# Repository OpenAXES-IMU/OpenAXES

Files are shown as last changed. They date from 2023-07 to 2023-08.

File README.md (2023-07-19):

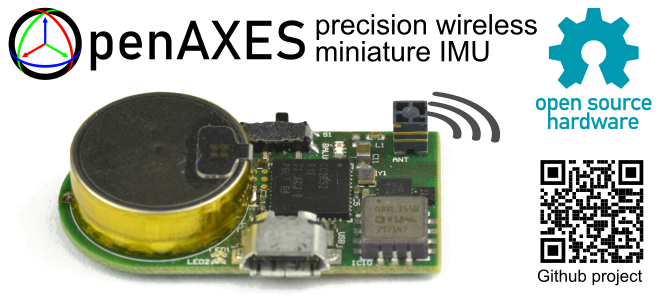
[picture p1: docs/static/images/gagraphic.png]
OpenAXES Graphical Abstract


# OpenAXES

**Hardware design files and source code for an open-access wireless IMU** developed at the [Institute of Microelectronic Systems](https://www.ims.uni-hannover.de/) at the Leibniz University Hannover, Germany.

The OpenAXES IMU is open-source hardware licensed under the CERN-OHL-S-v2+. This means that you are allowed to modify, share, or sell the design, **if** you adhere to the respecitive licenses (see section [License](#license) or [LICENSE.txt](/LICENSE.txt) for details).

If you use the OpenAXES project (or parts of it) in scientific work, please see the [Citation](#citation) section below.

## Hardware

The hardware subdirectory contains the ECAD design files for the OpenAXES PCB and its fabrication outputs, and MCAD files for the housing, the programming adapter, and a calibration fixture.

More information about the hardware and how to fabricate it can be found in [the README in the hardware folder](/hardware/README.md)

## Firmware

The OpenAXES firmware is written in C and based on the CC2652 SDK from Texas Instruments.
It is based on TI-RTOS and can be compiled with [Code Composer Studio (CCS)](https://www.ti.com/tool/CCSTUDIO).

More information on how to compile and flash the firmware can be found in [the README in the firmware folder](/firmware/README.md)

## Citation

If you use the OpenAXES project (or parts of it) in scientific work,
please cite our upcoming paper (**submitted for peer review - not published yet**).

> Title: "OpenAXES: An Open-Source Wireless Inertial Measurement Unit"
>
> Authors: Fritz Webering, Nils Stanislawski, Joseph Winkler, Sarah Kleinjohann, Holger Blume
>
> Journal: [IEEE Sensors Letters](https://ieee-sensors.org/ieee-sensors-letters/)

The correct precise citation will be updated as soon as possible.

# License

Copyright 2023 Nils Stanislawski (nils.stanislawski@ims.uni-hannover.de) and Fritz Webering (fritz.webering@ims.uni-hannover.de)

This documentation describes Open Hardware and is licensed under the CERN-OHL-S-v2 or any later version.

You may redistribute and modify this documentation under the terms of the CERN OHL-S-v2 (https://ohwr.org/cern_ohl_s_v2.txt) or any later version. This documentation is distributed WITHOUT ANY EXPRESS OR IMPLIED WARRANTY, INCLUDING OF MERCHANTABILITY, SATISFACTORY QUALITY AND FITNESS FOR A PARTICULAR PURPOSE. Please see the CERN OHL v2-S for applicable conditions

Source Location: https://github.com/OpenAXES-IMU/OpenAXES

For detailed license information on individual files, please see the file [LICENSE.txt](/LICENSE.txt) in the root folder of this repository.

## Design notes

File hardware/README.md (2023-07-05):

# Hardware

The **Hardware** subdirectory contains the ECAD design files for the OpenAXES PCB and its fabrication outputs, and MCAD files for the housing and calibration fixture.

This documentation describes Open Hardware and is licensed under the CERN-OHL-S v2 or any later version. See [License](#license) below for more information.

## PCB

This directory comprises the Altium Designer and KiCad EDA files. 
Altium Designer is a globally renowned PCB and electronic design software. 
KiCad, on the other hand, is a free open source software suite for EDA. 
The use of these two platforms ensures our project is accessible to a broad range of users.

The OpenAXES hardware platform was originally developed using Altium Designer.
To allow for the use of open source EDA software tools it has been ported to KiCad.
Known differences in the design files are only found in the silkscreen layers, so that there are no restrictions on the underlying functionality of the PCB.

### Getting Started

To work with the files contained in this directory, you will need to have the appropriate software installed on your local machine.

- For Altium files, download and install [Altium Designer](https://www.altium.com/)
- For KiCad files, download and install [KiCad EDA](https://www.kicad.org/)

Once you have installed the appropriate software, clone the repository and navigate to the respective subdirectories to access the project files.

### Fabrication outpus

Fabrication outputs are provided in the _PCB/Altium/Project Outputs for OpenAXES_ subdirectory.
Output files for both single PCB and a panel optimized for mass production are included.
 
### Deprecated components

- **BMI160**; pin-compatible replacement: BMI270

## Housing

The housing for the OpenAXES IMU can be found in the **hardware/case** subdirectory.
It was designed in FreeCAD 0.20 for 3D-printing with a 0.4 mm diameter FDM nozzle.
If the 3D printer is tunes correctly, the two halves of the case will snap together and provide a tight fit for the PCB.

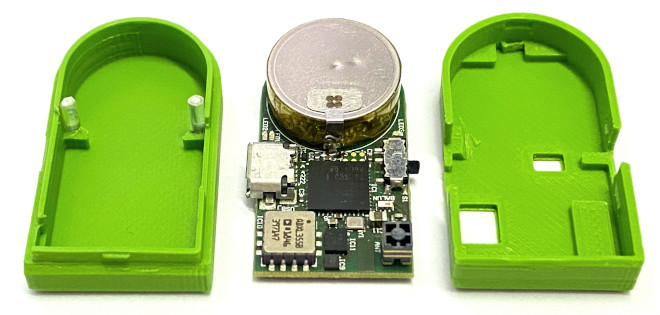
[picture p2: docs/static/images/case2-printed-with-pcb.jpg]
Photograph of the OpenAXES PCB and case


There are cutouts for the USB port, the power switch, the analog pads on the bottom of the PCB, and for the JTAG adapter.
The two holes at the top can be plugged with short pieces of transparent 3D-printing filament (1.75 mm diameter).
These will act as light guides for the top LEDs next to the battery.

## Programming adapter

The programming adapter found in the **hardware/programming-adapter** directory comprises a 3D-printable fixture and a single-layer PCB with spring loaded pins.
These work together with the case, holding the IMU in place and contacting the six pads on the underside of the IMU PCB, for JTAG programming or debugging.

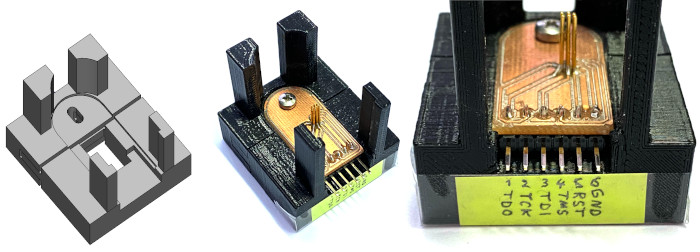
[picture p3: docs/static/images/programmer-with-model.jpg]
3D model and photograph of the programming adapter


The adapter can be used with any JTAG adapter compatible with the CC2652 processor and the Code Composer Studio IDE.
During development, we used the LAUNCHXL-CC26X2R1 evaluation board from TI as a JTAG programmer.
All JTAG signals on that board are accessible on a pin header, which is normally populated with jumpers.
By removing the jumpers, the JTAG interface on the evaluation board can be used for external boards:

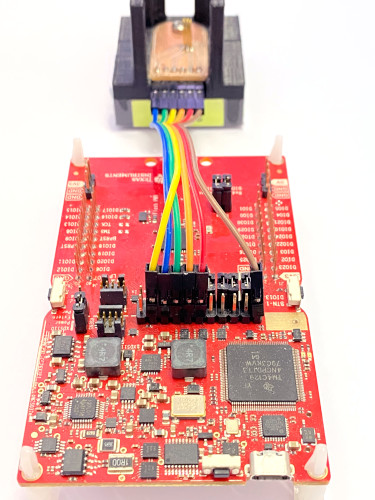
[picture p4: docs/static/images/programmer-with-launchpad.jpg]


## Calibration fixture

The calibration fixture found in **hardware/calibrator** is an icosahedron (20-sided polyhedron) with a recess that accepts the IMU case.
This fixture can be used together the with scripts in the **calibration** directory to obtain the sensor calibration coefficients for each individual unit.

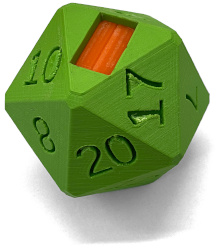
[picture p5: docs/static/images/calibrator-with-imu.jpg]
Photograph of the calibration fixture with an IMU


# License

Copyright 2023 Nils Stanislawski and Fritz Webering

This documentation describes Open Hardware and is licensed under the CERN-OHL-S-v2 or any later version.

You may redistribute and modify this documentation under the terms of the CERN OHL-S-v2 (https://ohwr.org/cern_ohl_s_v2.txt) or any later version. This documentation is distributed WITHOUT ANY EXPRESS OR IMPLIED WARRANTY, INCLUDING OF MERCHANTABILITY, SATISFACTORY QUALITY AND FITNESS FOR A PARTICULAR PURPOSE. Please see the CERN OHL v2-S for applicable conditions

Source Location: https://github.com/IMS-AS-LUH/OpenAXES

For detailed license information on individual files, please see the file [LICENSE.txt](/LICENSE.txt) in the root folder of this repository.

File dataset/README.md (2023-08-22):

# OpenAXES Example Robot Dataset

**Since git repositories are not suitable for storing large amounts of static data, the dataset itself is kept in the research data repository of the LUH: https://doi.org/10.25835/psqqs9w0. This repository just contains the Jupyter Notebook for quick access.**

This dataset was recorded using four OpenAXES IMUs mounted on the segments of a robot arm (UR5 by Universal Robots), as shown in Fig. 4.
The robot arm was programmed to perform a calibration movement, then trace a 2D circle or triangle in the air with its tool center point (TCP), and return to its starting position, at four different speeds from 100 mm/s to 250 mm/s.
This results in a total of 8 different scenarios (2 shapes times 4 speeds).
The ground truth joint angle and TCP position values were obtained from the robot controller.
The calibration movement at the beginning of the measurement allows for calculating the exact orientation of the sensors on the robot arm.

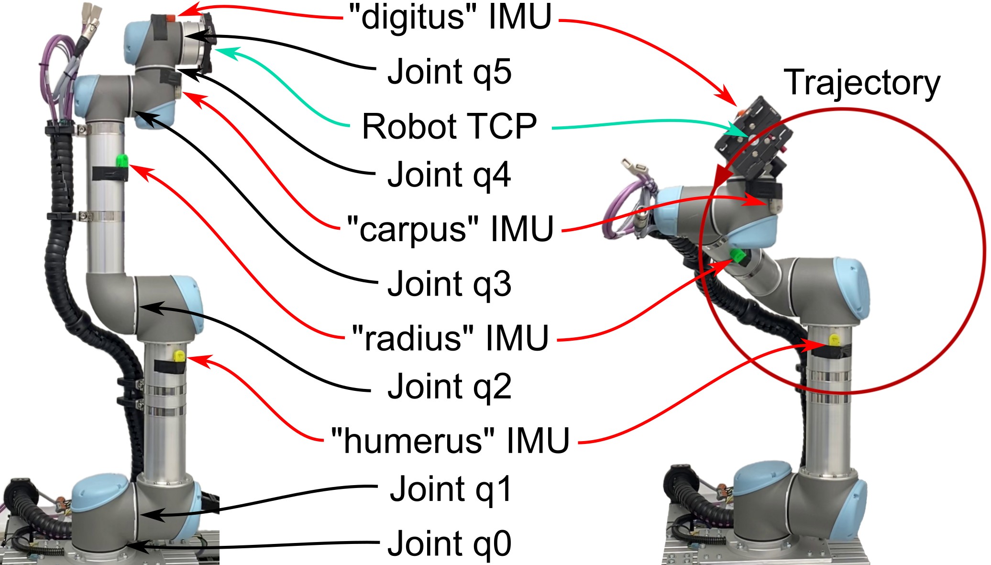
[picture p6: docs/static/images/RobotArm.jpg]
Fig. 4 Setup of the robot arm experiment, showing the four IMUs, the six joints of the robot arm, the tool center position (TCP) and the circle trajectory.
<br>
*Fig. 4  Setup of the robot arm experiment, showing the four IMUs, the six joints of the robot arm, the tool center position (TCP) and the circle trajectory.*

The IMUs were configured to send the raw data from the three gyroscope axes and the six accelerometer axes to a PC via BLE with 16 bit resolution per axis and 100 Hz sample rate.
Since no data packets were lost during this process, this dataset allows comparing and tuning different sensor fusion algorithms on the recorded raw data while using the ground truth robot data as a reference.

In order to visualize the results, the quaternion sequences from the IMUs were applied to the individual segments of a 3D model of the robot arm.
The end of this kinematic chain represents the TCP of the virtual model, which should ideally move along the same trajectory as the ground truth, barring the accuracy of the IMUs.
Since the raw sensor data of these measurements is available, the calibration coefficients can also be applied ex-post.

Since there are are 6 joints but only 4 IMUS, some redundancy must be exploited.
The redundancy comes from the fact that each IMU has 3 rotational degrees of fredom, but each joint has only one:

* The data for `q0` and `q1` are both derived from the orientation of the "humerus" IMU.
* `q2` is the difference<sup>†</sup> between the orientation of the "humerus" and "radius" IMUs.
* `q3` is the difference between the orientation of the "radius" and "carpus" IMUs.
* `q4` is the difference between the orientation of the "carpus" and "digitus" IMUs.
* The joint `q5` does not influence the position of the TCP, only its orientation, so it is ignored in the evaluation.
* <sup>†</sup> *Of course, difference here means not the subtraction of the quaternions but the rotational difference, which is the `R1 * inv(R0)` for two quaternions (or rotations) `R0` and `R1`. The actual code works a bit differently, but this describes the general principle.*

## Data

* Data recorded from the IMUs is in the directory `measure_raw-2022-09-15/`, one folder per scenario.
In those folders, there is one CSV file per IMU.
* Data recorded from the robot arm is in the directory `measure_raw-2022-09-15/robot/`, one CSV and MAT file per scenario.
* Some photos and videos of the recording process can be found in `Media`. Videos are stored in [git lfs](https://git-lfs.com/).

## Evaluation

The file `openaxes-example-robot-dataset.ipynb` is provided to play around with the data in the dataset and demonstrate how the files are read and interpreted.
To use the notebook, set up a Python 3 virtual environment and therein install the necessary packets with `pip install -r resuirements.txt`.
In order to view the graphs contained in the ipynb file, you will most likely have to trust the notebook beforehand, using the following command:

```bash
jupyter trust openaxes-example-robot-dataset.ipynb
```

**Beware:** This notebook is not a comprehensive evaluation and any results and plots shown in the file are not necessarily scientifically sound evidence of anything.

The notebook will store intermediate files in the `measure_raw-2022-09-15` directory, like the quaternion files calculated by the different filters, or the files containing the reconstructed TCP positions.
All intermediate files should be ignored by the file `measure_raw-2022-09-15/.gitignore`.

The generated intermediate files are also provided in the file `measure_raw-2022-09-15.tar.bz2`, in case you want to inspect the generated files without running the the notebook.

## Tools

A number of tools are used in the evaluation notebook.
Below is a short overview, but not a complete specification.
If you need to understand the input and output formats for each tool, please read the code.

* The file `calculate-quaternions.py` is used in the evaluation notebook to compute different attitude estimation filters like Madgwick or VQF on the raw accelerometer and gyroscrope measurements at 100 Hz.
* The directory `madgwick-filter` contains a small C program that applies the original Madgwick filter to a CSV file containing raw measurements and prints the results. It is used by `calculate-quaternions.py`.
* The file `calculate-robot-quaternions.py` calculates a CSV file of quaternions equivalent to the IMU quaternions from a CSV file containing the joint angles of the robot.
* The program `dsense_vis` mentioned in the notebook is used to calculate the 3D model of the robot arm from quaternions and determine the mounting orientations of the IMUs on the robot arm.
  This program will be released at a future date.
  In the meantime, the output files of `dsense_vis` are provided in the file `measure_raw-2022-09-15.tar.bz2`, which contains the complete content of the `measure_raw-2022-09-15` directory after executing the whole notebook.
  Just unpack this archive and merge its contents with the `measure_raw-2022-09-15` directory.
  This allows you to explore the reconstructed TCP files for the filters implemented at the time of publication.

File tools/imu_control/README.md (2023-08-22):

# OpenAXES IMU Tools

This directory contains scripts to communicate with, control, and configure the OpenAXES IMU.

This documentation describes Open Hardware and is licensed under the CERN-OHL-S v2 or any later version. See [License](#license) below for more information.

# Usage of imu_control.py

The `imu_control` script can be used to control the OpenAXES IMU via the Bluetooth Low Energy (BLE) GATT interface.
It also serves as a demonstration how to implement other clients for the GATT interface.

The main features of the script are:
* selecting which measurement data the IMU should send
* receiving measurement data from the IMU via BLE notifications
* recording the measurement data in CSV files
* passing the IMU data on to other processes via UDP
* showing status information like battery state or firmware version
* configuring the IMU, for example the calibration coefficients
* assistive functions for recording calibration datasets

## Prerequisites

* Use a Linux PC (preferably a modern Ubuntu) or VirtualBox and a Bluetooth adapter.
  The ASUS USB-BT400 stick works best in our experience, especially for many simultaneous connections to different IMUs.
  If you use VirtualBox, you can pass through the USB stick to the guest operating system.
* Make sure that gatttool is installed (probably `sudo apt install bluez bluez-tools`)
* Set permissions on hcitool:
  ```
  sudo setcap 'cap_net_raw,cap_net_admin+eip' /usr/bin/hcitool
  ```
  This allows normal users to scan for BLE devices using `hcitool lescan`.
  The udpstream script uses this to set the connection interval using `hcitool lecup ...` to avoid package loss.

## Configuration files

All operations that interact with an IMU expect a BLE MAC address on the command line.
If you do not like to memorize MAC addresses, you can assign arbitrary names to your IMUs and store them in a file called `my_imu_addresses.json` in the following format:
```json
{
    "imu1": "18:04:ED:C4:75:01",
    "imu2": "18:04:ED:C4:75:02"
}
```
These IMU names can then be used on the command line as shown in the examples below.

## Initialize IMUs before each use

* Switch IMUs on.
* Lay IMUs *perfectly still* on a table (LED side up).
* Run `./imu_control.py --reset-sensors imuX` for each IMU. *Do not touch IMUs before all commands completed!*
* IMU initialization is complete. You can now capture data.
  For example, run `./imu_control.py imuX` for each IMU to capture quaternions.
  Make a small pause between starting different IMUs, for example like this:

  ```
  ../imu_control.py imu1
  sleep 0.5
  ../imu_control.py imu2
  sleep 0.5
  ../imu_control.py imu6
  ```

## Lost packets at the start

* At the start of the transmission, some packets may be lost.
  This is normal, because the connection interval is set only a short while after the transmission starts.
* You can skip the first few packets and start recording once the connection is stable:
  `./imu_control.py imuX --skip 100` will skip the first 100 received packets before recording, which is about 1 second.
  Skipped packets will not be reported as "lost".

## Change what type of data is sent

* Reset IMUs (see above).
* Capture data using the `--mode` option.
  For example, `./imu_control.py --mode INDEX,ACCEL_BMI160,GYRO` will record a 16-bit packet index, plus gyroscope and accelerometer data from the BMI160 chip.
* See `./imu_control.py --help` for available data types for `--mode`.

## Battery level

* Battery level is permanently shown by the red blinking LED.
  The duty cycle is equal to the battery level (e.g. 40% on and 60% off means 40% battery level remaining).
* `./imu_control.py imuX -b` or `--battery` will print the battery level before each measurement.
* A WARNING will be printed if the battery level is below 15% when starting a measurement.
* `./imu_control.py imuX --status` will print detailed battery information, like current consumption, voltage, etc.
* The battery is charged via Micro USB. The blue charging LED will turn off when the battery is full.

## Enable/disable calibration

* Calibration coefficients are applied to the raw data by default, if calibration data is found in IMU flash memory.
* Run `./imu_control.py imuX --status` to see `calibration_status`.
  Value `0x00` means disabled, `0x01` means enabled, and anything else is an error.
* Disable use of calibration coefficients (until IMU reboot):
  `./imu_control.py imuX --command USE_CALIBRATION 0` to disable calibration.
* Run `./imu_control.py --command USE_CALIBRATION 1` to enable calibration.
* Write new calibration coefficients to flash memory on the IMU.
  **You must** replace the ones and zeros with the actual calibration coefficients for each unit according to [the calibration instructions](/calibration/README.md).
  ```
  ./imu_control.py imuX --write-calibration-full 'COEFFICIENTS'
  ```
  
  The argument `'COEFFICIENTS'` must be a space-separated and quoted list of 36 floating point numbers.
  These numbers are three 3x3 identity calibration matrices and three 3-element zero bias vectors:
  1. 9 Coefficients in [row-major order](https://en.wikipedia.org/wiki/Row-_and_column-major_order) for the 3x3 ADXL355 accelerometer scale and nonlinearity calibration matrix.
  2. 3 Coefficients for the ADXL355 bias vector.
  3. 9 Coefficients in [row-major order](https://en.wikipedia.org/wiki/Row-_and_column-major_order) for the BMI160 accelerometer scale and nonlinearity calibration matrix.
  4. 3 Coefficients for the BMI160 accelerometer bias vector.
  5. 9 Coefficients in [row-major order](https://en.wikipedia.org/wiki/Row-_and_column-major_order) for the BMI160 gyroscope scale and nonlinearity calibration matrix.
  6. 3 Coefficients for the BMI160 gyroscope bias vector.
* Permanently reset all calibration coefficients to their default uncalibrated state by setting the calibration matrices to identity and the bias vectors to zero with the following command:
  ```
  ./imu_control.py imuX --write-calibration-full '1 0 0  0 1 0  0 0 1   0 0 0   1 0 0  0 1 0  0 0 1   0 0 0   1 0 0  0 1 0  0 0 1   0 0 0'
  ```

# Usage of bleak_imu_control.py

This script is an experimental port of an old version of `imu_control.py` to use Python 3 and [the python package `bleak`](https://bleak.readthedocs.io/en/latest/) instead of `gatttool` invocations.
Since we could not get the `bleak` interface to work reliably with our IMU, we suspended the experiment and continued using the `gatttool` version that worked more or less reliably.

The current version of the script is presented here only for documentation purposes.
It could be used as a starting point in case someone wants to resume the effort of porting to Python 3 with `bleak`.

# License

Copyright 2023 Nils Stanislawski and Fritz Webering

This documentation describes Open Hardware and is licensed under the CERN-OHL-S-v2 or any later version.

You may redistribute and modify this documentation under the terms of the CERN OHL-S-v2 (https://ohwr.org/cern_ohl_s_v2.txt) or any later version. This documentation is distributed WITHOUT ANY EXPRESS OR IMPLIED WARRANTY, INCLUDING OF MERCHANTABILITY, SATISFACTORY QUALITY AND FITNESS FOR A PARTICULAR PURPOSE. Please see the CERN OHL v2-S for applicable conditions

Source Location: https://github.com/IMS-AS-LUH/OpenAXES

For detailed license information on individual files, please see the file [LICENSE.txt](/LICENSE.txt) in the root folder of this repository.

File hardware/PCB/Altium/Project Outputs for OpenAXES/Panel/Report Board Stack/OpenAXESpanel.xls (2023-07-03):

Board Stack Report
Stack Up |  | Layer Stack
Layer | Board Layer Stack | Name | Material | Thickness | Constant
1 |  | Top Paste
2 |  | Top Overlay
3 |  | Top Solder | Solder Resist | 0,010mm | 3,5
4 |  | Top Layer | Copper | 0,035mm
5 |  | Dielectric 1 | PP-016 | 0,115mm | 4,4
6 |  | Dielectric 2 | PP-016 | 0,115mm | 4,4
7 |  | L2 | Copper | 0,035mm
8 |  | Dielectric 3 | Core-032 | 0,356mm | 4,7
9 |  | L3 | Copper | 0,035mm
10 |  | Dielectric 4 | PP-016 | 0,115mm | 4,4
11 |  | Dielectric 5 | PP-016 | 0,115mm | 4,4
12 |  | Bottom Layer | Copper | 0,035mm
13 |  | Bottom Solder | Solder Resist | 0,010mm | 3,5
14 |  | Bottom Overlay
15 |  | Bottom Paste
 | Height : 0,976mm

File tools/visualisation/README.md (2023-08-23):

# IMU Quaternion Visualization

The folder `/tools/visualization/UDP_Quaternion_OpenGL_Visualisation` contains a Qt project to visualize the Quaternions received from an OpenAXES IMU.

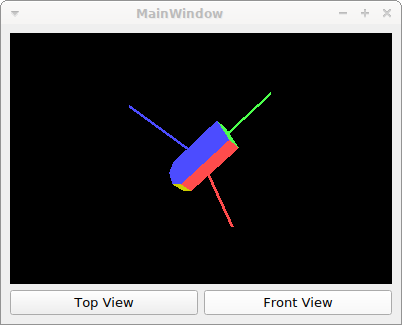
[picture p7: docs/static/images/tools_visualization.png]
Screenshot of visualization software, showing a 3D rendering of the IMU


It receives Quaternions via UDP from the `imu_control.py` script, which will send out one UDP packet to localhost for every received BLE notification.
By default, UDP port 1024 wille, but that can be changed by changing the line `#define UDP_PORT 1024` in `mainwindow.cpp`, and with the second positional command line argument for the script (see `imu_control.py --help`).

From each incoming UDP packet, the four signed 16-bit integers that represent the quaternion will be extracted.
The resulting quaternions will be visualized using a 3D-model of the IMU in OpenGL.

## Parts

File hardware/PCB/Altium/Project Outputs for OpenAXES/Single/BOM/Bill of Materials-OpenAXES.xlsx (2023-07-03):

Line # | Name | Description | Designator | Quantity | Document | Manufacturer 1 | Manufacturer Part Number 1 | Manufacturer Lifecycle 1 | Supplier 1 | Supplier Part Number 1 | Supplier Order Qty 1 | Supplier Unit Price 1 | Supplier Stock 1 | Supplier Packaging 1 | Supplier Subtotal 1 | Case Size/Dimension | Case-EIA | Case-Metric
 | ANTENNA |  | ANT | 1 | C:\Users\Public\Documents\Altium\OpenAXES\SoC.SchDoc | Molex | 47948-0001 |  | Mouser | 538-47948-0001 | 1 | 1.95 | 20907 | Tape & Reel | 1.95
 | 2450BM14G0011 |  | BALUN | 1 | C:\Users\Public\Documents\Altium\OpenAXES\SoC.SchDoc | Johanson | 2450BM14G0011T | Volume Production | Mouser | 609-2450BM14G0011T | 1 | 0.5 | 27734 | Tape & Reel | 0.5
 | CP1654 A3 |  | BAT | 1 | C:\Users\Public\Documents\Altium\OpenAXES\Battery.SchDoc
 | 100n 16V 0402 | CAP 100nF 16V ±10% 0402 (1005 Metric) Thickness 0.6mm SMD | C1, C2, C3, C5, C6, C14, C16, C26, C29, C33, C36, C38, C40, C41, C42, C43, C44 | 17 | C:\Users\Public\Documents\Altium\OpenAXES\SoC.SchDoc, C:\Users\Public\Documents\Altium\OpenAXES\Battery.SchDoc, C:\Users\Public\Documents\Altium\OpenAXES\USB2UART.SchDoc, C:\Users\Public\Documents\Altium\OpenAXES\Sensors.SchDoc | Kyocera AVX | 0402YD104KAT2A | Volume Production | Mouser | 581-0402YD104K | 17 | 0.013 | 3009473 | Tape & Reel | 0.221 |  | 0402 | 1005
 | 10u 6V3 0402 | CAP 10uF 6.3V ±20% 0402 (1005 Metric) Thickness 0.6mm SMD | C4, C21, C22 | 3 | C:\Users\Public\Documents\Altium\OpenAXES\SoC.SchDoc, C:\Users\Public\Documents\Altium\OpenAXES\Battery.SchDoc | Samsung | CL05A106MQ5NUNC | Volume Production | Mouser | 187-CL05A106MQ5NUNC | 3 | 0.24 | 655718 | Tape & Reel | 0.72 |  | 0402 | 1005
 | 12p 10V 0402 | CAP 12pF 10V ±1% 0402 (1005 Metric) Thickness 0.6mm SMD | C7, C8 | 2 | C:\Users\Public\Documents\Altium\OpenAXES\SoC.SchDoc | Vishay Vitramon | VJ0402A120FXQCW1BC |  | Mouser | 77-VJ0402A120FXQCBC | 2 | 0.25 | 8101 | Tape & Reel | 0.5 |  | 0402 | 1005
 | 1p3 10V 0402 | CAP 1.3pF 10V ±0.25pF 0402 (1005 Metric) Thickness 0.6mm SMD | C9 | 1 | C:\Users\Public\Documents\Altium\OpenAXES\SoC.SchDoc | KEMET | CBR04C139B5GAC | Volume Production | Mouser | 80-CBR04C139B5GAC | 1 | 0.16 | 18397 |  | 0.16 |  | 0402 | 1005
 | 1u 16V 0402 | CAP 1uF 16V ±10% 0402 (1005 Metric) Thickness 0.6mm SMD | C10, C20, C23, C30, C31, C34, C35, C37, C39 | 9 | C:\Users\Public\Documents\Altium\OpenAXES\SoC.SchDoc, C:\Users\Public\Documents\Altium\OpenAXES\Battery.SchDoc, C:\Users\Public\Documents\Altium\OpenAXES\Sensors.SchDoc | Taiyo Yuden | EMK105BJ105MVHF | Not Recommended for New Design | Mouser | 963-EMK105BJ105MVHF | 10 | 0.071 | 207971 | Tape & Reel | 0.71 |  | 0402 | 1005
 | CAP 22u 6.3V 0805 | CAP 22uF 6.3V ±10% 0805 (2012 Metric) Thickness 1.45mm SMD | C11 | 1 | C:\Users\Public\Documents\Altium\OpenAXES\SoC.SchDoc | KEMET | C0805C226K9PACTU | Volume Production | Mouser | 80-C0805C226K9PACTU | 1 | 0.35 | 67178 | Tape & Reel | 0.35 |  | 0805 | 2012
 | 4u7 10V 0603 | CAP 4.7uF 10V ±20% 0603 (1608 Metric) Thickness 1mm SMD | C12, C13, C18, C25, C32 | 5 | C:\Users\Public\Documents\Altium\OpenAXES\Battery.SchDoc, C:\Users\Public\Documents\Altium\OpenAXES\USB2UART.SchDoc, C:\Users\Public\Documents\Altium\OpenAXES\Sensors.SchDoc | KEMET | C0603C475M8PACTU | Volume Production | Mouser | 80-C0603C475M8P | 5 | 0.23 | 41855 | Tape & Reel | 1.15 |  | 0603 | 1608
 | 470n 6V3 0402 | CAP 470nF 6.3V ±10% 0402 (1005 Metric) Thickness 0.6mm SMD | C15 | 1 | C:\Users\Public\Documents\Altium\OpenAXES\Battery.SchDoc | Yageo | CC0402KRX5R5BB474 | Volume Production | Mouser | 603-CC402KRX5R5BB474 | 1 | 0.1 | 243770 | Tape & Reel | 0.1 |  | 0402 | 1005
 | 220p 10V 0402 | CAP 220pF 10V ±5% 0402 (1005 Metric) Thickness 0.6mm SMD | C17 | 1 | C:\Users\Public\Documents\Altium\OpenAXES\Battery.SchDoc | Vishay Vitramon | VJ0402Y221JXQCW1BC |  | Mouser | 77-VJ0402Y221JXQCBC | 1 | 0.13 | 17875 | Tape & Reel | 0.13 |  | 0402 | 1005
 | 2u2u 6V3 0402 | CAP 2.2uF 6.3V ±10% 0402 (1005 Metric) Thickness 0.6mm SMD | C19 | 1 | C:\Users\Public\Documents\Altium\OpenAXES\Battery.SchDoc | Kyocera AVX | 04026D225KAT2A | Volume Production | Mouser | 581-04026D225KAT2A | 1 | 0.18 | 126807 | Tape & Reel | 0.18 |  | 0402 | 1005
 | 10n 16V 0402 | CAP 10nF 16V ±10% 0402 (1005 Metric) Thickness 0.33mm SMD | C24 | 1 | C:\Users\Public\Documents\Altium\OpenAXES\USB2UART.SchDoc | Murata | GRM15XR71C103KA86D | Not Recommended for New Design | Mouser | 81-GRM15XR71C103KA6D | 1 | 0.13 | 73728 | Tape & Reel | 0.13 |  | 0402 | 1005
 | 47p 16V 0402 | CAP 47pF 16V ±10% 0402 (1005 Metric) Thickness 0.6mm SMD | C27, C28 | 2 | C:\Users\Public\Documents\Altium\OpenAXES\USB2UART.SchDoc | Vishay Vitramon | VJ0402A470KXJCW1BC |  | Mouser | 77-VJ0402A470KXJCBC | 2 | 0.11 | 18228 | Tape & Reel | 0.22 |  | 0402 | 1005
 | TPD1E10B06DPYR | ESD in 0402 Package with 10 pF Capacitance and 6 V Breakdown, 1 Channel, -40 to +125 degC, 2-pin X2SON (DPY), Green (RoHS & no Sb/Br) | D1, D2 | 2 | C:\Users\Public\Documents\Altium\OpenAXES\USB2UART.SchDoc | Texas Instruments | TPD1E10B06DPYR | Volume Production | Mouser | 595-TPD1E10B06DPYR | 2 | 0.39 | 566012 | Tape & Reel | 0.78
 | CC2652R1FRGZT | CC2650 SimpleLink(TM) Multistandard Wireless MCU, 1.8 to 3.8 V, -40 to 85 degC, 48-Pin VFQFN, Green (RoHS & no Sb/Br), Tape and Reel | IC1 | 1 | C:\Users\Public\Documents\Altium\OpenAXES\SoC.SchDoc | Texas Instruments | CC2652R1FRGZR | Volume Production
 | MCP73830/L |  | IC2 | 1 | C:\Users\Public\Documents\Altium\OpenAXES\Battery.SchDoc | Microchip | MCP73830T-2AAI/MYY | Volume Production | Mouser | 579-MCP73830T2AAIMYY | 1 | 1.19 | 49256 | Tape & Reel | 1.19
 | MAX17055ETB+ |  | IC3 | 1 | C:\Users\Public\Documents\Altium\OpenAXES\Battery.SchDoc | Maxim | MAX17055ETB+T | Volume Production | Mouser | 700-MAX17055ETB+T | 1 | 2.65 | 71324 | Tape & Reel | 2.65
 | BQ2970x |  | IC4 | 1 | C:\Users\Public\Documents\Altium\OpenAXES\Battery.SchDoc | Texas Instruments | BQ29700DSET | Volume Production | Mouser | 595-BQ29700DSET | 1 | 1.22 | 2900 | Tape & Reel | 1.22
 | LTC3221EDC | Micropower, Regulated Charge Pump, 1.8 to 5.5 V Vin, Adjustable Vout, 6-pin SON (DC6-6), -40 to 85 degC | IC5 | 1 | C:\Users\Public\Documents\Altium\OpenAXES\Battery.SchDoc | Analog Devices / Linear Technology | LTC3221EDC-5#TRMPBF | Volume Production | Mouser | 584-C3221EDC-5TRMPBF | 1 | 5.48 | 1335 | Tape & Reel | 5.48
 | TPS7A3501 |  | IC6 | 1 | C:\Users\Public\Documents\Altium\OpenAXES\Battery.SchDoc | Texas Instruments | TPS7A3501DRVT | Volume Production | Mouser | 595-TPS7A3501DRVT | 1 | 1.29 | 474 | Tape & Reel | 1.29
 | ECMF02-2AMX6 | Integrated Circuit | IC7 | 1 | C:\Users\Public\Documents\Altium\OpenAXES\USB2UART.SchDoc | STMicroelectronics | ECMF02-2AMX6 | Volume Production | Digi-Key | 497-10773-1-ND | 1 | 0.64 | 82842 | Cut Tape | 0.64
 | FT230XQ-R | USB to Basic UART Interface Chip, UHCI/OHCI/EHCI Compatible, USB 2.0 Compatible, -40 to +85 degC, 16-Pin QFN, Pb-Free, Tape and Reel | IC8 | 1 | C:\Users\Public\Documents\Altium\OpenAXES\USB2UART.SchDoc | FTDI | FT230XQ-R | Volume Production | Mouser | 895-FT230XQ-R | 1 | 2.46 | 83526 | Tape & Reel | 2.46
 | MMC3416XPJ |  | IC9 | 1 | C:\Users\Public\Documents\Altium\OpenAXES\Sensors.SchDoc | Memsic | MMC34160PJ |  | Mouser | 438-MMC34160PJ | 1 | 4.08 | 4100 | Tape & Reel | 4.08
 | ADXL355BEZ | Low Noise, Low Drift, Low Power, 3-Axis MEMS Accelerometer, 2.25 to 3.6 V, -40 to 125 degC, 14-Pin LCC (E-14-1), RoHS, Tray | IC10 | 1 | C:\Users\Public\Documents\Altium\OpenAXES\Sensors.SchDoc | Analog Devices | ADXL355BEZ | Volume Production | Mouser | 584-ADXL355BEZ | 1 | 64.97 | 7122 | Tray | 64.97
 | BMI160 | Small, low Power Inertial Measurement Unit, 1.2 to 3.6 V, -40 to 85 degC, 14-Pin LGA, Halogen-Free, Tape and Reel | IC11 | 1 | C:\Users\Public\Documents\Altium\OpenAXES\Sensors.SchDoc | Bosch | BMI160
 | BMP388 |  | IC12 | 1 | C:\Users\Public\Documents\Altium\OpenAXES\Sensors.SchDoc | Bosch Sensortec | BMP388
 | LQP15MN1N8B02D | Chip Inductor, 1.8 nH, +/- 0.1 nH, 280 mA, -40 to 85 degC, 0402 (1005 Metric), RoHS, Tape and Reel | L1 | 1 | C:\Users\Public\Documents\Altium\OpenAXES\SoC.SchDoc | Murata | LQP15MN1N8B02D | Obsolete | Mouser | 81-LQP15MN1N8B02D | 1 | 0.18 | 38535 | Tape & Reel | 0.18 | 0402
 | 742792605 | SMD EMI Suppression Ferrite Bead WE-CBF, Z = 33 Ohm | L2 | 1 | C:\Users\Public\Documents\Altium\OpenAXES\USB2UART.SchDoc | Wurth Electronics | 742792605 | Volume Production | Mouser | 710-742792605 | 1 | 0.15 | 6553 | Tape & Reel | 0.15
 | GREEN | Generic 0402 LED | LED1 | 1 | C:\Users\Public\Documents\Altium\OpenAXES\SoC.SchDoc | Rohm | SML-P11MTT86R | Volume Production | Mouser | 755-SML-P11MTT86R | 1 | 0.43 | 175055 | Tape & Reel | 0.43
 | RED | Generic 0402 LED | LED2 | 1 | C:\Users\Public\Documents\Altium\OpenAXES\SoC.SchDoc | Rohm | SML-P11VTT86 | Obsolete | Digi-Key | 846-SML-P11VTT86CT-ND | 1 | 0.55 | 20148 |  | 0.55
 | BLUE | Generic 0402 LED | LED3 | 1 | C:\Users\Public\Documents\Altium\OpenAXES\Battery.SchDoc | Rohm | SMLP13BC8TT86 | Obsolete
 | ORANGE | Generic 0402 LED | LED4 | 1 | C:\Users\Public\Documents\Altium\OpenAXES\USB2UART.SchDoc | Rohm | SML-P11DTT86 | Obsolete | Digi-Key | 846-SML-P11DTT86CT-ND | 1 | 0.54 | 42202 |  | 0.54
 | YELLOW | Generic 0402 LED | LED5 | 1 | C:\Users\Public\Documents\Altium\OpenAXES\USB2UART.SchDoc | Rohm | SML-P11YTT86 | Obsolete | Mouser | 755-SML-P11YTT86 | 1 | 0.58 | 19756 | Tape & Reel | 0.58
 | PressureSensor |  | PS | 1 | C:\Users\Public\Documents\Altium\OpenAXES\Sensors.SchDoc
 | 10K 1% 0402 | 10K 0.063W 1% 0402 (1005 Metric) SMD | R1, R2, R3, R9, R23, R24 | 6 | C:\Users\Public\Documents\Altium\OpenAXES\SoC.SchDoc, C:\Users\Public\Documents\Altium\OpenAXES\Battery.SchDoc, C:\Users\Public\Documents\Altium\OpenAXES\Sensors.SchDoc |  |  |  |  |  |  |  |  |  |  |  | 0402 | 1005
 | Jumper 0402 | Jumper 0402 (1005 Metric) | R4, R20, R22 | 3 | C:\Users\Public\Documents\Altium\OpenAXES\SoC.SchDoc, C:\Users\Public\Documents\Altium\OpenAXES\USB2UART.SchDoc | Bourns | CR0402-J/-000GLF | Volume Production | Mouser | 652-CR0402-J/-000GLF | 10 | 0.004 | 4210905 | Tape & Reel | 0.04 |  | 0402 | 1005
 | 3K3 5% 0402 | 3K3 0.063W 5% 0402 (1005 Metric) SMD | R5, R6, R8, R17, R18 | 5 | C:\Users\Public\Documents\Altium\OpenAXES\SoC.SchDoc, C:\Users\Public\Documents\Altium\OpenAXES\Battery.SchDoc, C:\Users\Public\Documents\Altium\OpenAXES\USB2UART.SchDoc | Panasonic | ERJ-2GEJ332X | Volume Production | Mouser | 667-ERJ-2GEJ332X | 10 | 0.015 | 513572 | Tape & Reel | 0.15 |  | 0402 | 1005
 | 1K2 1% 0402 | 1K2 0.063W 1% 0402 (1005 Metric) SMD | R7 | 1 | C:\Users\Public\Documents\Altium\OpenAXES\Battery.SchDoc | Bourns | CR0402-FX-1201GLF | Volume Production | Mouser | 652-CR0402FX-1201GLF | 1 | 0.1 | 773686 | Tape & Reel | 0.1 |  | 0402 | 1005
 | 0R01 5% 0402 |  | R10 | 1 | C:\Users\Public\Documents\Altium\OpenAXES\Battery.SchDoc | Panasonic | ERJ-MFBAF10MX
 | 2K2 5% 0402 | 2K2 0.063W 5% 0402 (1005 Metric) SMD | R11 | 1 | C:\Users\Public\Documents\Altium\OpenAXES\Battery.SchDoc | Panasonic | ERJ-2GEJ222X | Volume Production | Mouser | 667-ERJ-2GEJ222X | 1 | 0.1 | 451901 | Tape & Reel | 0.1 |  | 0402 | 1005
 | 330R 5% 0402 | 330R 0.063W 5% 0402 (1005 Metric) SMD | R12 | 1 | C:\Users\Public\Documents\Altium\OpenAXES\Battery.SchDoc | Yageo | RC0402JR-07330RL | Volume Production | Mouser | 603-RC0402JR-07330RL | 1 | 0.1 | 1083538 | Tape & Reel | 0.1 |  | 0402 | 1005
 | 4M99 1% 0402 | 4M99 0.063W 1% 0402 (1005 Metric) SMD | R13, R14 | 2 | C:\Users\Public\Documents\Altium\OpenAXES\Battery.SchDoc | Yageo | RC0402FR-074M99L | Volume Production | Mouser | 603-RC0402FR-074M99L | 10 | 0.015 | 10310 | Tape & Reel | 0.15 |  | 0402 | 1005
 | 47K 1% 0402 | 47K 0.063W 1% 0402 (1005 Metric) SMD | R15 | 1 | C:\Users\Public\Documents\Altium\OpenAXES\Battery.SchDoc | Yageo | RC0402FR-0747KL | Volume Production | Mouser | 603-RC0402FR-0747KL | 1 | 0.1 | 2650692 | Tape & Reel | 0.1 |  | 0402 | 1005
 | 24K3 1% 0402 | 24K3 0.063W 1% 0402 (1005 Metric) SMD | R16 | 1 | C:\Users\Public\Documents\Altium\OpenAXES\Battery.SchDoc | Bourns | CR0402-FX-2432GLF | Volume Production | Mouser | 652-CR0402FX-2432GLF | 1 | 0.1 | 347312 | Tape & Reel | 0.1 |  | 0402 | 1005
 | 27R 5% 0402 | 27R 0.063W 5% 0402 (1005 Metric) SMD | R19, R21 | 2 | C:\Users\Public\Documents\Altium\OpenAXES\USB2UART.SchDoc | Panasonic | ERJ-2GEJ270X | Volume Production | Mouser | 667-ERJ-2GEJ270X | 10 | 0.015 | 199037 | Tape & Reel | 0.15 |  | 0402 | 1005
 | SWITCH_SPDT |  | S1 | 1 | C:\Users\Public\Documents\Altium\OpenAXES\Battery.SchDoc | Alps Electric | SSSS810701 |  | Mouser | 688-SSSS810701 | 1 | 1.21 | 7180 | Tape & Reel | 1.21
 | DUAL_NMOS |  | T1 | 1 | C:\Users\Public\Documents\Altium\OpenAXES\Battery.SchDoc | ON Semiconductor / Fairchild | FDMA2002NZ | Volume Production | Mouser | 512-FDMA2002NZ | 1 | 0.9 | 1403 | Tape & Reel | 0.9
 | HIRO-ZX62R-B-5P-5 |  | USB | 1 | C:\Users\Public\Documents\Altium\OpenAXES\USB2UART.SchDoc | Hirose | ZX62R-B-5P(30) | Volume Production | Mouser | 798-ZX62R-B-5P30 | 1 | 1.02 | 22445 | Tape & Reel | 1.02
 | CON_6P2R |  | X1 | 1 | C:\Users\Public\Documents\Altium\OpenAXES\SoC.SchDoc
 | NX2016SA-48M |  | Y1 | 1 | C:\Users\Public\Documents\Altium\OpenAXES\SoC.SchDoc | NDK | NX2016SA-48M-EXS00A-CS08718 |  | Mouser | 344-NX2016SA48S08718 | 1 | 0.74 | 3419 | Tape & Reel | 0.74
 | FC-135-32.76 | Crystal Unit, 32 to 77.5 KHz, 0.5 uW, -40 to 85 degC, 2-Pin SMD, RoHS | Y2 | 1 | C:\Users\Public\Documents\Altium\OpenAXES\SoC.SchDoc | Epson | FC-13532.7680KA-AG0 | Volume Production | Mouser | 732-FC135-32.76KAAG0 | 1 | 0.61 | 477751 | Tape & Reel | 0.61

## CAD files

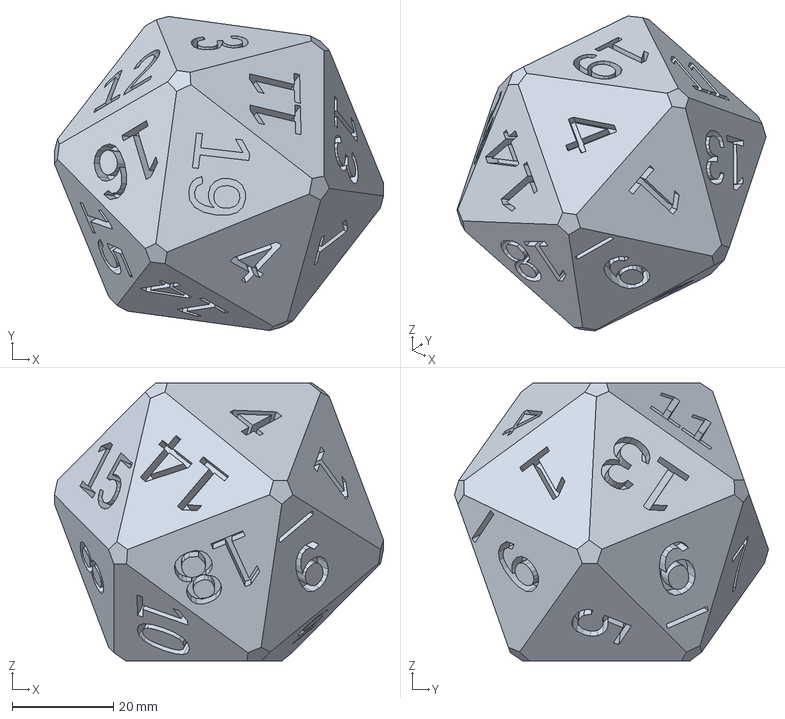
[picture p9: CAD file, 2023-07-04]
hardware/calibrator/D20-Calibrator.3mf
65.2 x 62.1 x 55.0 mm

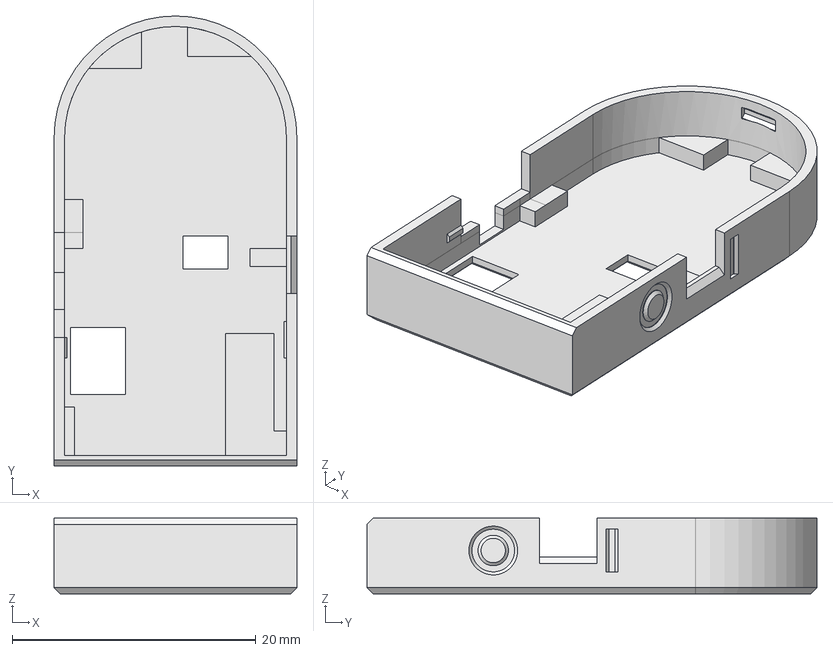
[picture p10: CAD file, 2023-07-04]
hardware/case/IMU-Case2_v12-Bottom.step
19.9 x 36.9 x 6.20 mm

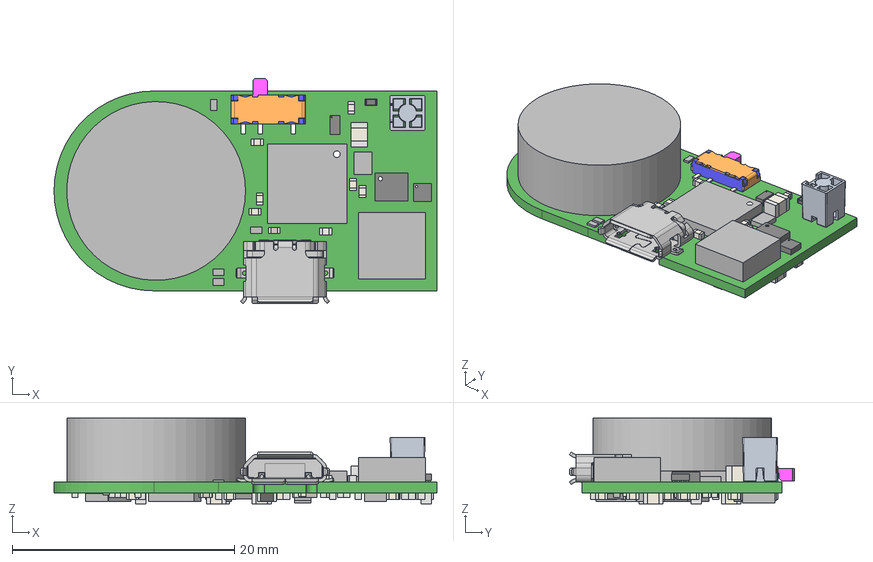
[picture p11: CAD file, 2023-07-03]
hardware/PCB/Altium/Project Outputs for OpenAXES/Single/ExportSTEP/OpenAXES.step
34.5 x 20.3 x 7.74 mm
Extruded x 223
PinsArrayLR
SSSS810701
Pin_Shape x 14
ball x 16
Thermal_Shape x 4
ZX62R-B-5P

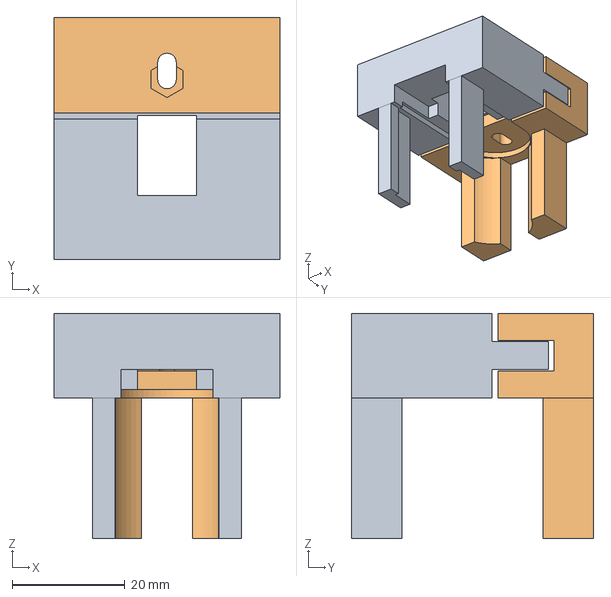
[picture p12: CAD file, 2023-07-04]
hardware/programming-adapter/3D/OpenAXES-Programming-Adapter.step
40.1 x 43.0 x 40.0 mm

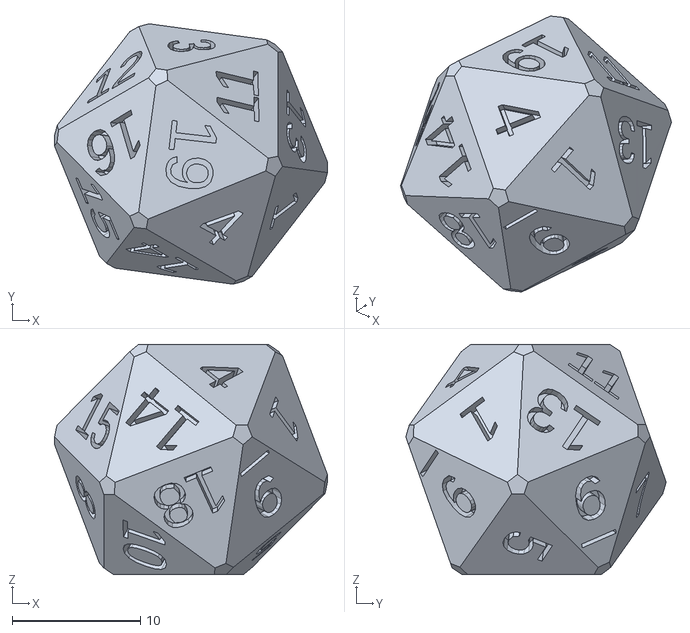
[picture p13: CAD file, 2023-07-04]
hardware/calibrator/sides_20_standard.stl
21.3 x 20.3 x 18.0

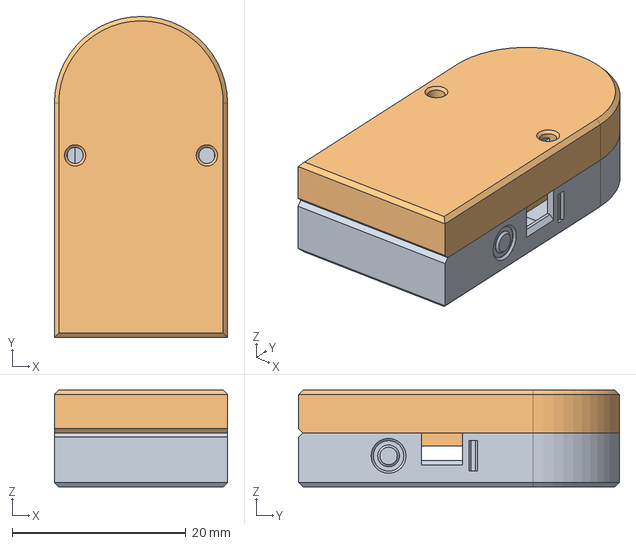
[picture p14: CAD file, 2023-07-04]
hardware/case/IMU-Case2_v12.FCStd
19.9 x 36.9 x 11.1 mm
Bottom
Top

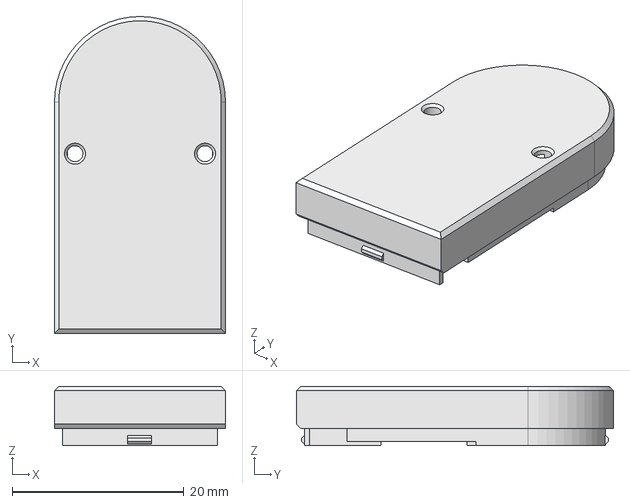
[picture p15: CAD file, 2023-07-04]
hardware/case/IMU-Case2_v12-Top.step
19.9 x 36.9 x 6.90 mm

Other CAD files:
hardware/case/IMU-Case2_v12-Bottom.stl
hardware/case/IMU-Case2_v12-Top.stl
hardware/programming-adapter/3D/OpenAXES-Programming-Adapter.FCStd
hardware/programming-adapter/3D/OpenAXES-Programming-Adapter.stl

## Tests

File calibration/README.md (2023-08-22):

# OpenAXES Calibration Tools and Example Dataset

The `calibration` subdirectory contains the scripts used to calculate the calibration coefficients for OpenAXES IMUs (or any other suitable IMU) using the method published by Tedaldi et al. in their 2014 paper [A robust and easy to implement method for IMU calibration without external equipments][1]

For calibrating our own IMUs we [used the MATLAB implementation by Jianzhu Huai][2] (state as of 2017).
The `imu_tk_matlab` code is included in this repository as a submodule only, because it has no license that would permit us to include a copy of the code itself.
We made some changes, improvements, and bugfixes to the original code, which are contained in the [patches](/calibration/matlab/patches/) subdirectory.
The changes are described in the `CHANGES.md` inside the patch, as well as in greater detail in [our preprint on arxiv.org][3].

Alternatively, one could try to use [the original C++ implementation by Tedaldi et al.][4], which is released under the BSD license.
We used the MATLAB version because it was easier to get started.
We did not test whether it also works with [Octave](https://octave.org/), a free implementation of the MATLAB language.

## Example Calibration Dataset

The subdirectory `/calibration/openaxes_example_calibration_dataset` contains example calibration recordings from four OpenAXES IMUs, which can be used to explore and understand the calibration algorithm.
Please refer to the [separate README file for the dataset](/calibration/openaxes_example_calibration_dataset/README.md) for more information.

**Since git repositories are not suitable for storing large amounts of static data, the dataset itself is kept in the research data repository of the LUH: https://doi.org/10.25835/oimsodoy. Download the dataset from there and extract it into the `/calibration` directory in this repository.**

## Recording Calibration Data

We recommend using the icosahedral calibration fixture for reliable and repeatable recording of calibration data for the OpenAXES IMU.
The 3D-printable model can be found in [the /hardware/calibrator/ directory](/hardware/calibrator/D20-Calibrator.3mf) in 3MF format for PrusaSlicer.

Detailed step-by-step instructions for recording a calibration sequence can be found in [the dataset README file](/calibration/openaxes_example_calibration_dataset/README.md#dataset-recording).

## Calculating Calibration Coefficients

Once calibration recordings have been performed, the `imu_tk` algorithm can be used to calculate the corrective calibration coefficients for that IMU.
We recommend doing a few practice runs before calibrating units for production use.
It is possible and recommended to perform multiple calibration recordings for each IMU and compare the results to make sure they are consistent.
Otherwise, small mistakes in the procedure in one calibration run could result in suboptimal calibration.

To use the MATLAB implementation of the `imu_tk` algorithm, you must first execute the following commands to obtain the patched `imu_tk_matlab` source code:
```bash
# Obtain original imu_tk_matlab code
git submodule update
# Apply changes and fixes to imu_tk_matlab
cd calibration/matlab/imu_tk_matlab
git apply ../patches/*.patch
# Start matlab in calibration directory
cd ../../
matlab
```
This should open MATLAB in the `calibration` directory in this repository (the one containing this README file).

In MATLAB you can run the file `matlab/OpenAXES/do_imu_calibration.m` to calculate the calibration coefficients based on one example recording in `log_imu9_2022-06-22_22-13-55.csv`.
Make sure that you are in the correct folder so that the `imu_tk_matlab` source files can be found somewhere in the matlab search path (see `path(...)` calls).

You can change the `filename` variable in `do_imu_calibration.m` in order to calculate calibration coefficients for your own IMUs.

## Applying Calibration Coefficients to IMUs

After calculating the calibration coefficients, the matlab script should print out command line arguments for `imu_control.py`, which can be used to permanently write the calculated coefficients to your IMU.
The following command line should be printed out for the example recording `log_imu9_2022-06-22_22-13-55.csv`:
```
imu_control.py imu9 --write-calibration-full="0.96276 0 0 0.0015751 0.96732 0 -0.00018891 0.000859 0.97079 0.064447 0.011034 0.034253 0.95418 0 0 0.0031573 0.96061 0 0.009235 0.00049713 0.9501 -0.033224 0.080497 0.01579 0.97288 0.0076747 -0.0063582 -0.011829 1.0062 -0.00033403 0.010087 0.00029571 1.0068 -0.00020494 0.00063007 -0.00036962"
```

Since the coefficients are stored in flash memory, they are retained across resets.
When restarting the IMU, the calibration coefficients should automatically be loaded from flash and applied to all measurements (raw data and quaternions), unless disabled via the corresponding GATT interface via `imu_control.py`.

More information about `imu_control.py` (e.g. enabling, disabling, or checking the current calibration status) can be found in [the corresponding README in `/tools/imu_control/`](/tools/imu_control/README.md).

## Contributing Changes to imu_tk_matlab

As mentioned above, the lack of a license in `imu_tk_matlab` project means that we can not include its source code into this repository, just our changes.
If you change anything in `imu_tk_matlab` and want to contribute your changes to the OpenAXES repository, please use the following procedure:

1. Commit your changes by using git inside the submodule folder `imu_tk_matlab`
2. Inside the submodule folder, run `git format-patch origin/master -o ../patches/`
3. Commit all new `.patch` files that were created into the OpenAXES repository.
4. Do _**NOT**_ <s>`git add imu_tk_matlab`</s>

[1]: https://doi.org/10.1109/ICRA.2014.6907297 "Paper 'A robust and easy to implement method for IMU calibration without external equipments' by Tedaldi et al."
[2]: https://github.com/JzHuai0108/imu_tk_matlab "Matlab scripts of David Tedaldi's ICRA14 paper, a robust and easy to implement method for IMU calibration by Jianzhu Huai"
[3]: https://arxiv.org/pdf/2207.04801.pdf "Preprint 'Improved Calibration Procedure for Wireless Inertial
Measurement Units without Precision Equipment' by Webering et al."
[4]: https://bitbucket.org/alberto_pretto/imu_tk "The original imu_tk C++ implementation"

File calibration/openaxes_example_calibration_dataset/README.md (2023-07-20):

# OpenAXES Example Calibration Dataset

**Since git repositories are not suitable for storing large amounts of static data, the dataset itself is kept in the research data repository of the LUH: https://doi.org/10.25835/oimsodoy. Download the dataset from there and extract it into the `/calibration` directory in this repository.**

This dataset contains calibration sequences of four OpenAXES IMUs, which were performed using the icosahedral calibration fixture described in the OpenAXES repository and paper.
For each IMU, five logs were recorded using the icosahedral calibration fixture according to the procedure described [below](#dataset-recording).
These can be found in the `logs` subdirectory.

Additionally, the `cuboid_logs` directory contains two logs for each IMU in which the device was only placed on the flat faces of the 3D-printed case.
As stated in the preprint, these are not useful for calibration and yield no usable calibration results.
They are only provided for completeness.

The `openaxes_example_calibration_dataset` subdirectory also contains the MATLAB scripts which were used to evaluate the dataset for [our preprint][3].
The script `coefficients-from-mat-files.py` can be used to extract the calibration coefficients from the `.mat` files.

## Evaluation

The `matlab_eval` subdirectory contains the scripts used to calculate the evaluation data presented in [our preprint][3].
To run it, you need the patched `imu_tk_matlab` code from the [OpenAXES repository](https://github.com/OpenAXES-IMU/OpenAXES) see the file [`/calibration/README.md`](https://github.com/OpenAXES-IMU/OpenAXES/blob/main/calibration/README.md) there.

## Dataset Recording

The example dataset was recorded for all four IMUs according to the procedure detailed below.

1. Make the environment as still as possible, for example:
   1. Choose a stury surface on which to perform the calibration, i.e. not a flimsy table that vibrates and sways with each touch.
   2. Avoid touching the surface on which you are working during the whole calibration procedure.
   3. Avoid walking around or moving on your chair during the whole calibration procedure.
   4. Remove all other people and other sources of movement from the room.
2. Insert the IMU into the 3D-printed case
3. Insert the case fully into the calibration fixture
4. Place the fixture on a flat surface in front of the operator who will perform the calibration movements
   A. Place the face with digit 1 facing upwards toward the ceiling
   B. Orient the digit 1 such that the operator can read it naturally (top side of the digit facing away from the operator).
5. Start recording the data with the following command:
   ```
   imu_control.py  imuX -b --still=3 --reset --skip=50 --mode=INDEX,ACCEL_ADXL355,ACCEL_BMI160,GYRO
   ```
   This command will start recording the raw accelerometer and gyroscope data from both inertial sensor chips on the IMU, along with an increasing 16 bit counter.
   * The argument `imuX` must be substituted with the designator of the IMU that is to be calibrated.
   * The flag `-b` will print battery state information to the console before the measurement starts.
   * The flag `--reset` will reset the internal state of the IMU before starting the measurement, specifically: *
     * Re-initialize the sensor ICs, e.g. performing gyroscope offset compensation
     * Reset the quaternion by calculating a new initial quaternion from the accelerometer data.
     * Reset the 16 bit INDEX counter
   * The argument `--still=3` emit a beeping sound when the IMU has lain still for 3 seconds after the last detected movement, prompting the operator to perform the next movement.
   * The argument `--skip=50` will discard the first 50 GATT notifications received, which corresponds to about half a second of data.
     This is necessary because the likelihood of packet loss is far greater at the beginning of the transmission due to unknown reasons.
6. Leave the IMU still on the surface for 40 seconds
7. Rotate the icosahedron such that the next numbered side faces up and is oriented correctly readable for the operator.
   * (_note:_ face number 2 contains the cutout for the IMU case and has no number)
   * It is helpful to draw a small arrow on each face, which points in the general direction of the next number, to speed up the time needed to find the correct face.
   * The movements should be practiced a few times to ensure smooth execution, because long periods of fumbling will increase the total calibration time, which might decrease the accuracy of the method.
8. Place the rotated icosahedron back on the flat surface and let it rest completely motionless until the beeping sound indicates that the static phase has been detected.
9. Again, make sure not to touch the table, walk around, or move on your chair during the still phase.
10. Repeat steps 7-9 for the next numbered face up until number 20.
11. After the first 20 faces, repeat steps 6-7 another 17-20 times, but rotate the icosahedron to a random face instead of the next numbered face.
12. After 37-40 faces, stop the recording by pressing `Ctrl+C` in the terminal running `imu_control.py`.

[1]: https://doi.org/10.1109/ICRA.2014.6907297 "Paper 'A robust and easy to implement method for IMU calibration without external equipments' by Tedaldi et al."
[2]: https://github.com/JzHuai0108/imu_tk_matlab "Matlab scripts of David Tedaldi's ICRA14 paper, a robust and easy to implement method for IMU calibration by Jianzhu Huai"
[3]: https://arxiv.org/pdf/2207.04801.pdf "Preprint 'Improved Calibration Procedure for Wireless Inertial
Measurement Units without Precision Equipment' by Webering et al."
[4]: https://bitbucket.org/alberto_pretto/imu_tk "The original imu_tk C++ implementation"

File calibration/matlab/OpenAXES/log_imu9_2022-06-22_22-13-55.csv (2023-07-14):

MAC | IMU | TIME | INDEX | QUATERNION_0 | QUATERNION_1 | QUATERNION_2 | QUATERNION_3 | ACCEL_ADXL355_0 | ACCEL_ADXL355_1 | ACCEL_ADXL355_2 | ACCEL_BMI160_0 | ACCEL_BMI160_1 | ACCEL_BMI160_2 | GYRO_0 | GYRO_1 | GYRO_2 | GYRO_ECC_0 | GYRO_ECC_1 | GYRO_ECC_2
18:04:ED:C4:75:1A | imu9 | 1655928838621431 | 51 | 0.000000 | 0.000000 | 0.000000 | 0.000000 | -0.063125 | 10.148750 | 0.255000 | -0.245000 | 10.262500 | 0.184375 | 0.000000 | 0.001065 | 0.000000 | 0 | 0 | 0
18:04:ED:C4:75:1A | imu9 | 1655928838636508 | 52 | 0.000000 | 0.000000 | 0.000000 | 0.000000 | -0.048750 | 10.162500 | 0.234375 | -0.252500 | 10.268750 | 0.203125 | 0.000000 | 0.001065 | -0.001065 | 0 | 0 | 0
18:04:ED:C4:75:1A | imu9 | 1655928838644102 | 53 | 0.000000 | 0.000000 | 0.000000 | 0.000000 | -0.030000 | 10.154375 | 0.239375 | -0.264375 | 10.288125 | 0.220625 | -0.001065 | 0.000000 | -0.001065 | 0 | 0 | 0
18:04:ED:C4:75:1A | imu9 | 1655928838651603 | 54 | 0.000000 | 0.000000 | 0.000000 | 0.000000 | -0.048125 | 10.166250 | 0.279375 | -0.236875 | 10.261250 | 0.239375 | 0.000000 | 0.000000 | -0.001065 | 0 | 0 | 0
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

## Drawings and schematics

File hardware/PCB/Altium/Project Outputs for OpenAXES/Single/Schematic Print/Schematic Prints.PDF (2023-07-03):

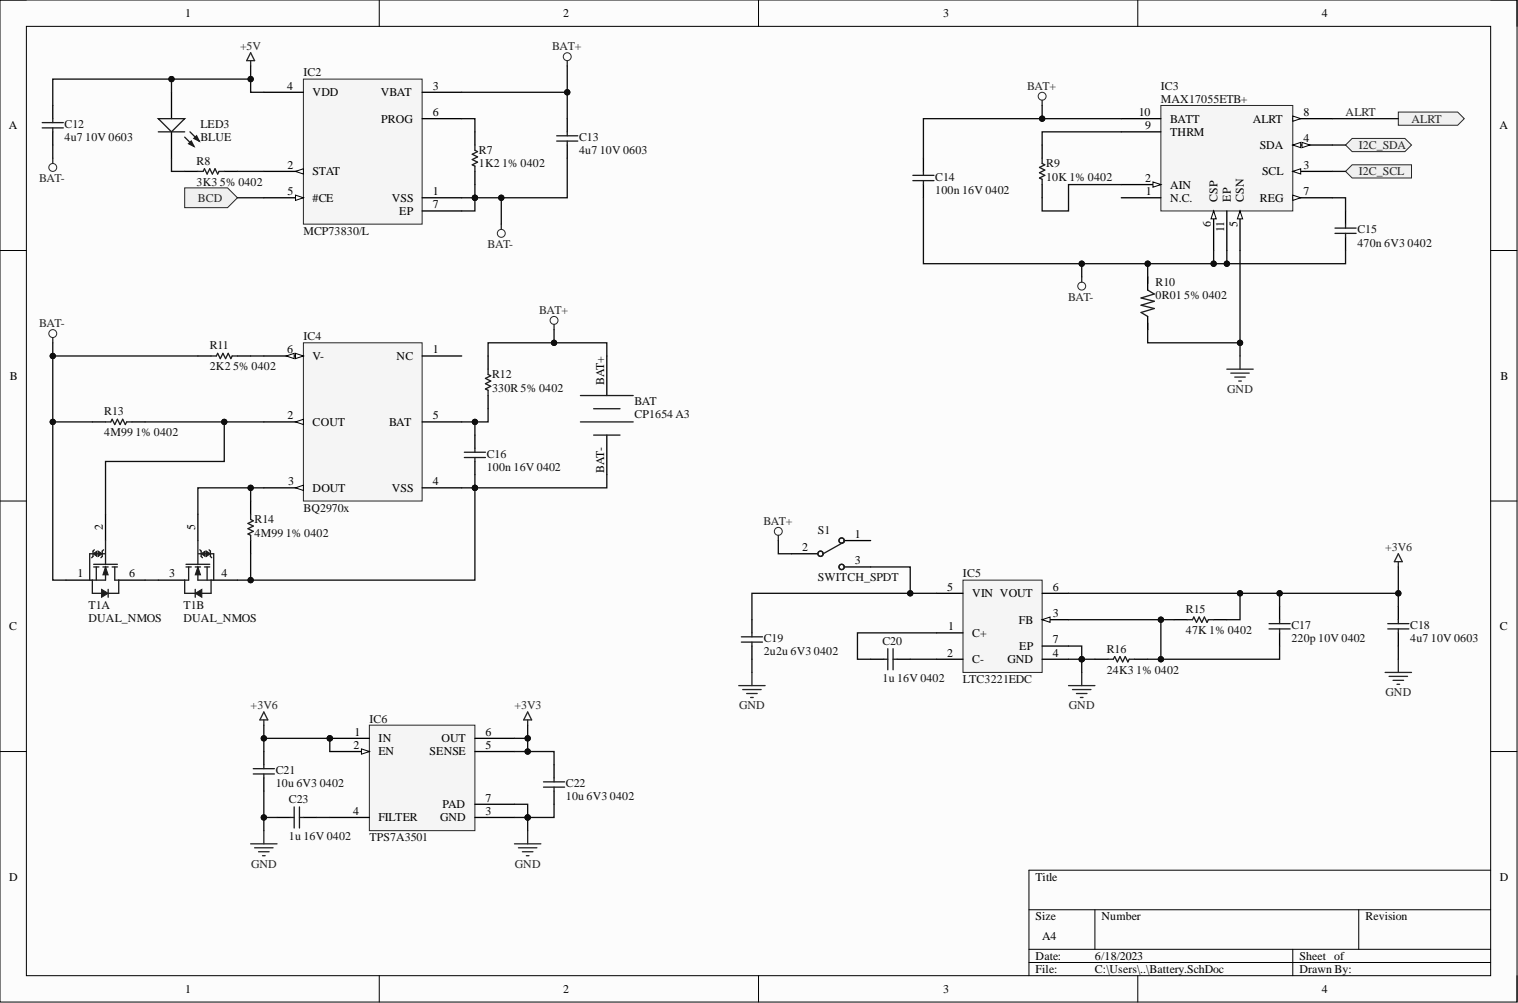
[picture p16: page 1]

R13 | 2K2 5% 0402 | COUT 2

R14
4M99 1% 0402

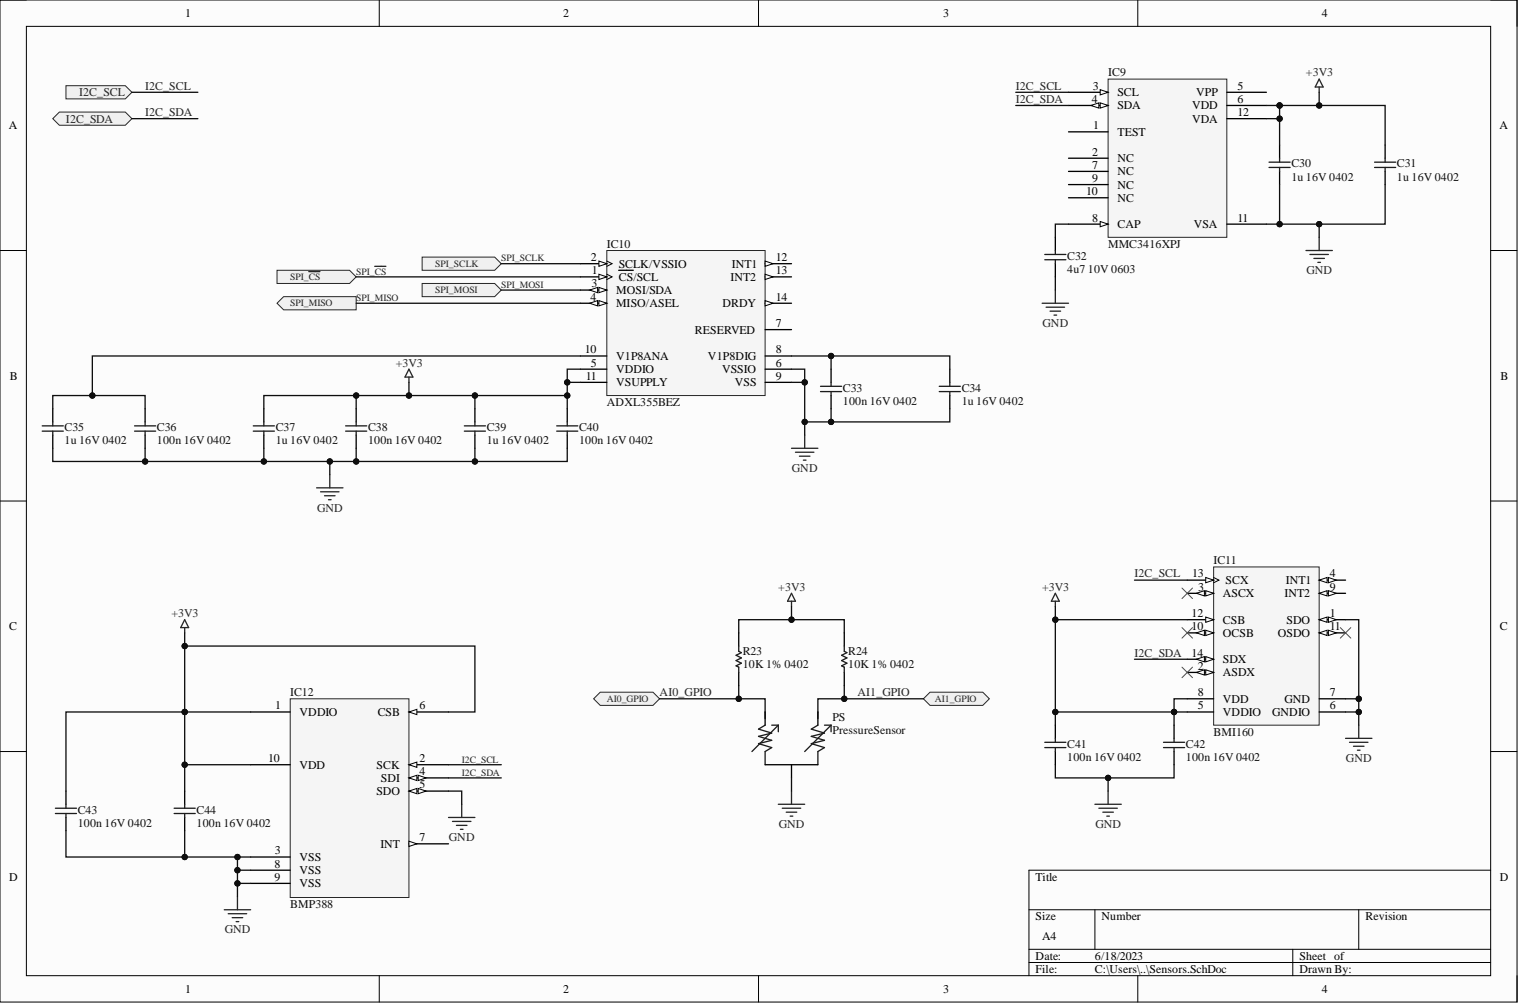
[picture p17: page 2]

VDD 10

VSS 8
VSS 9

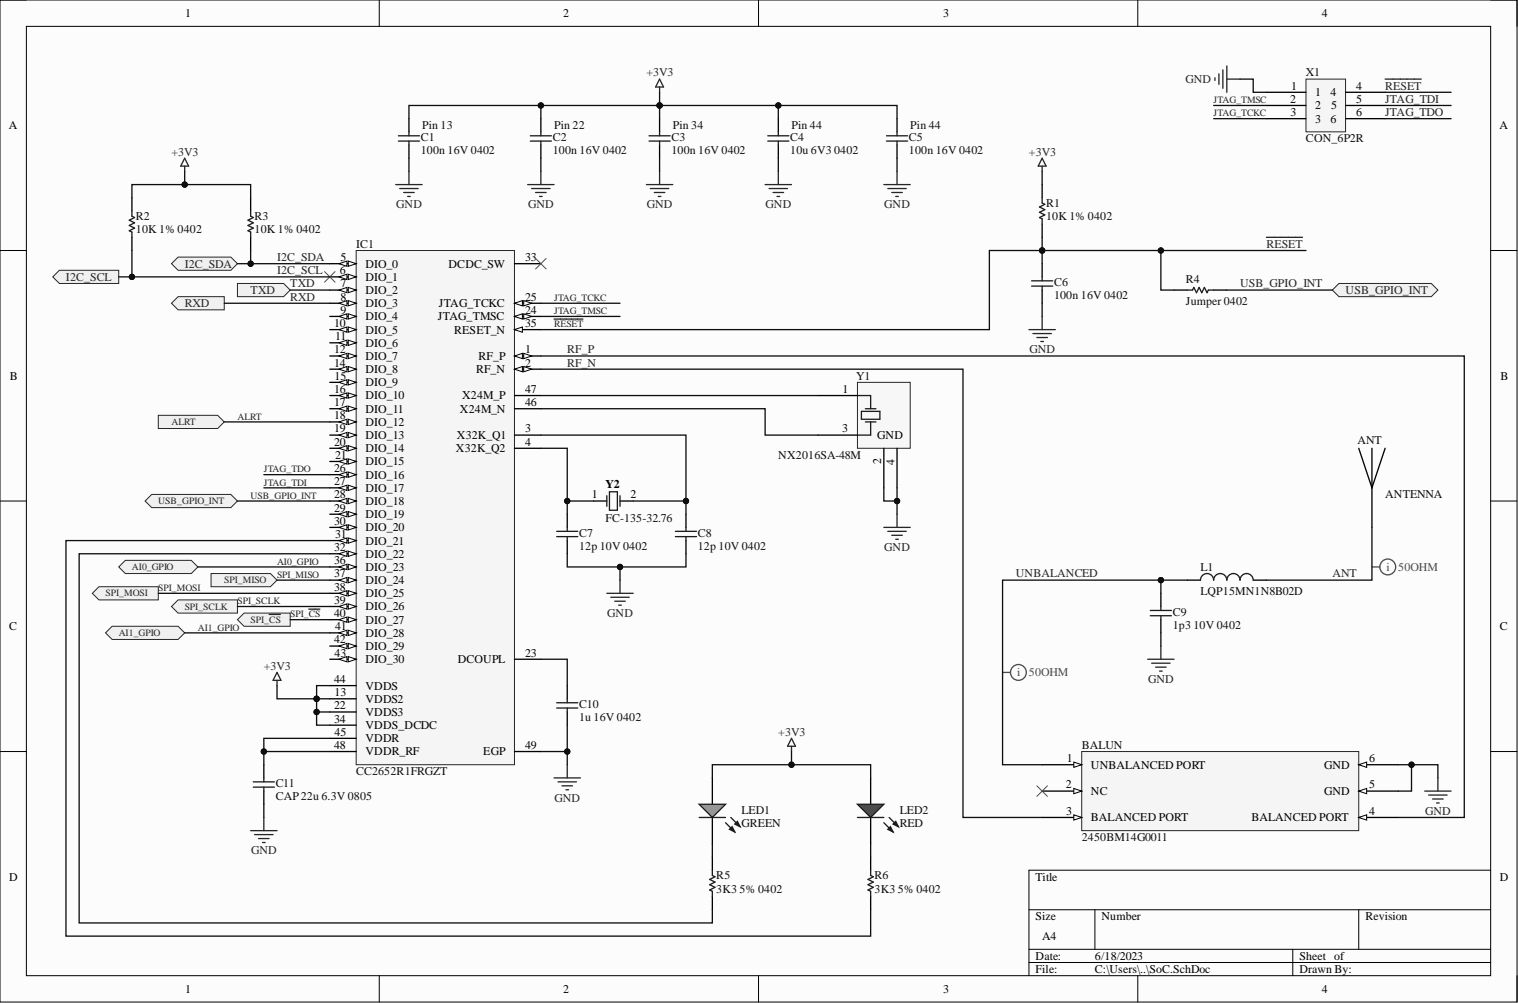
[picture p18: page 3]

2 | RF_ N
4 7 | Y 1

3 2 | DIO _ 2 2 | | 1 0 V 0 4 0 2

AI0_GP IO AI0_GPIO 3 6 3 7 S P I_M I S O S P I_M I S O I_MOS I S P I_S C L S P I_S C L K S P I_C AI1_GP | DIO _ 2 3 DIO _ 2 4 DIO _ 2 5 DIO _ 2 6 DIO _ 2 7 DIO _ 2 8 DIO _ 2 9 DIO _ 3 0 DCO U PL V D D S V D D S 2 V D D S 3 V D DS_ D C D C V D D R V D DR_ RF E G P | 2 3

1 3
2 2
3 4

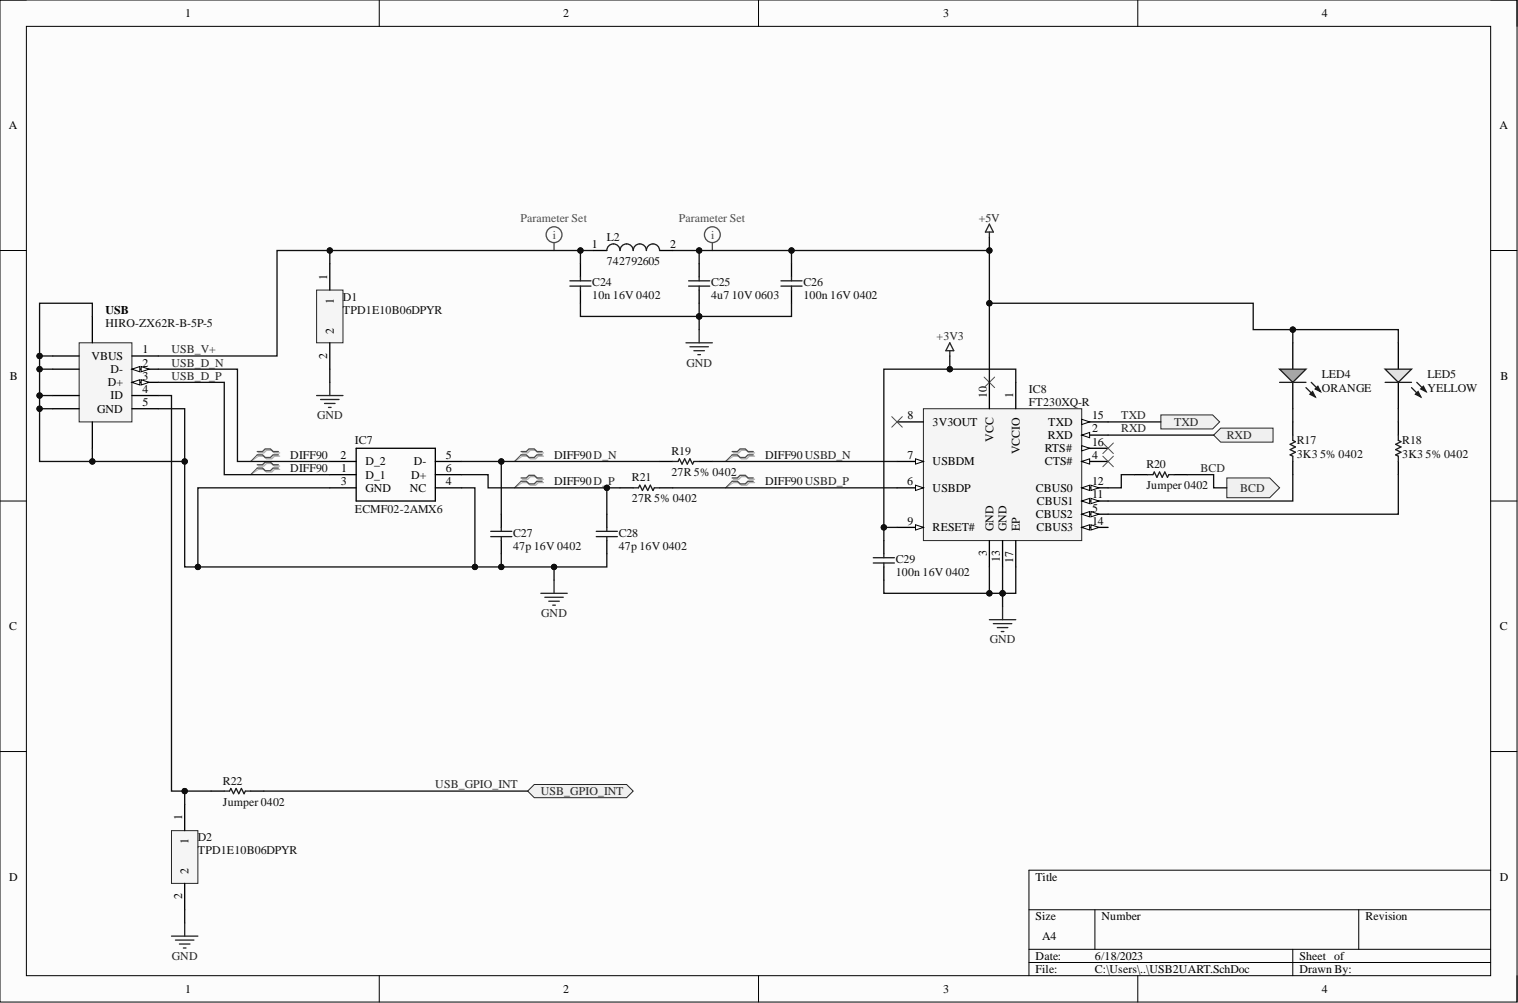
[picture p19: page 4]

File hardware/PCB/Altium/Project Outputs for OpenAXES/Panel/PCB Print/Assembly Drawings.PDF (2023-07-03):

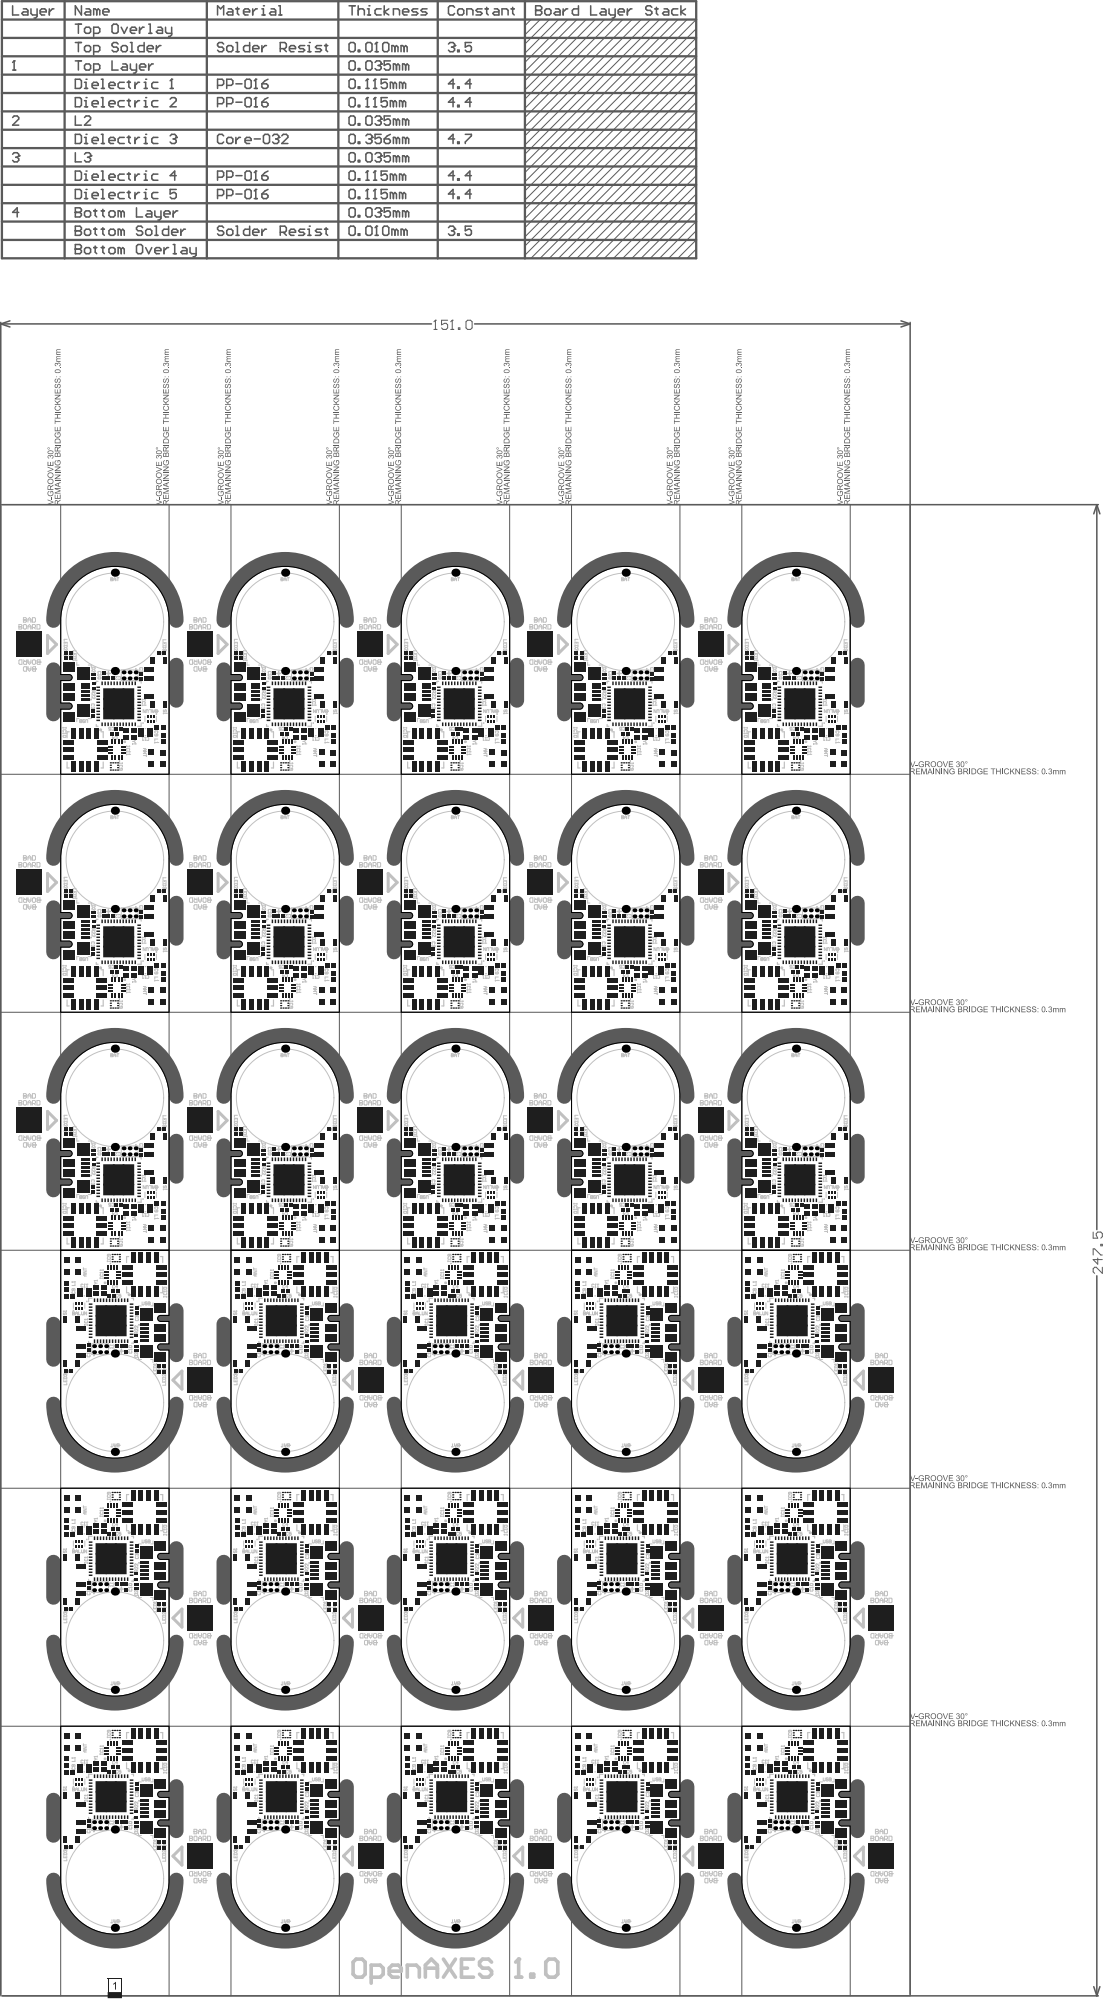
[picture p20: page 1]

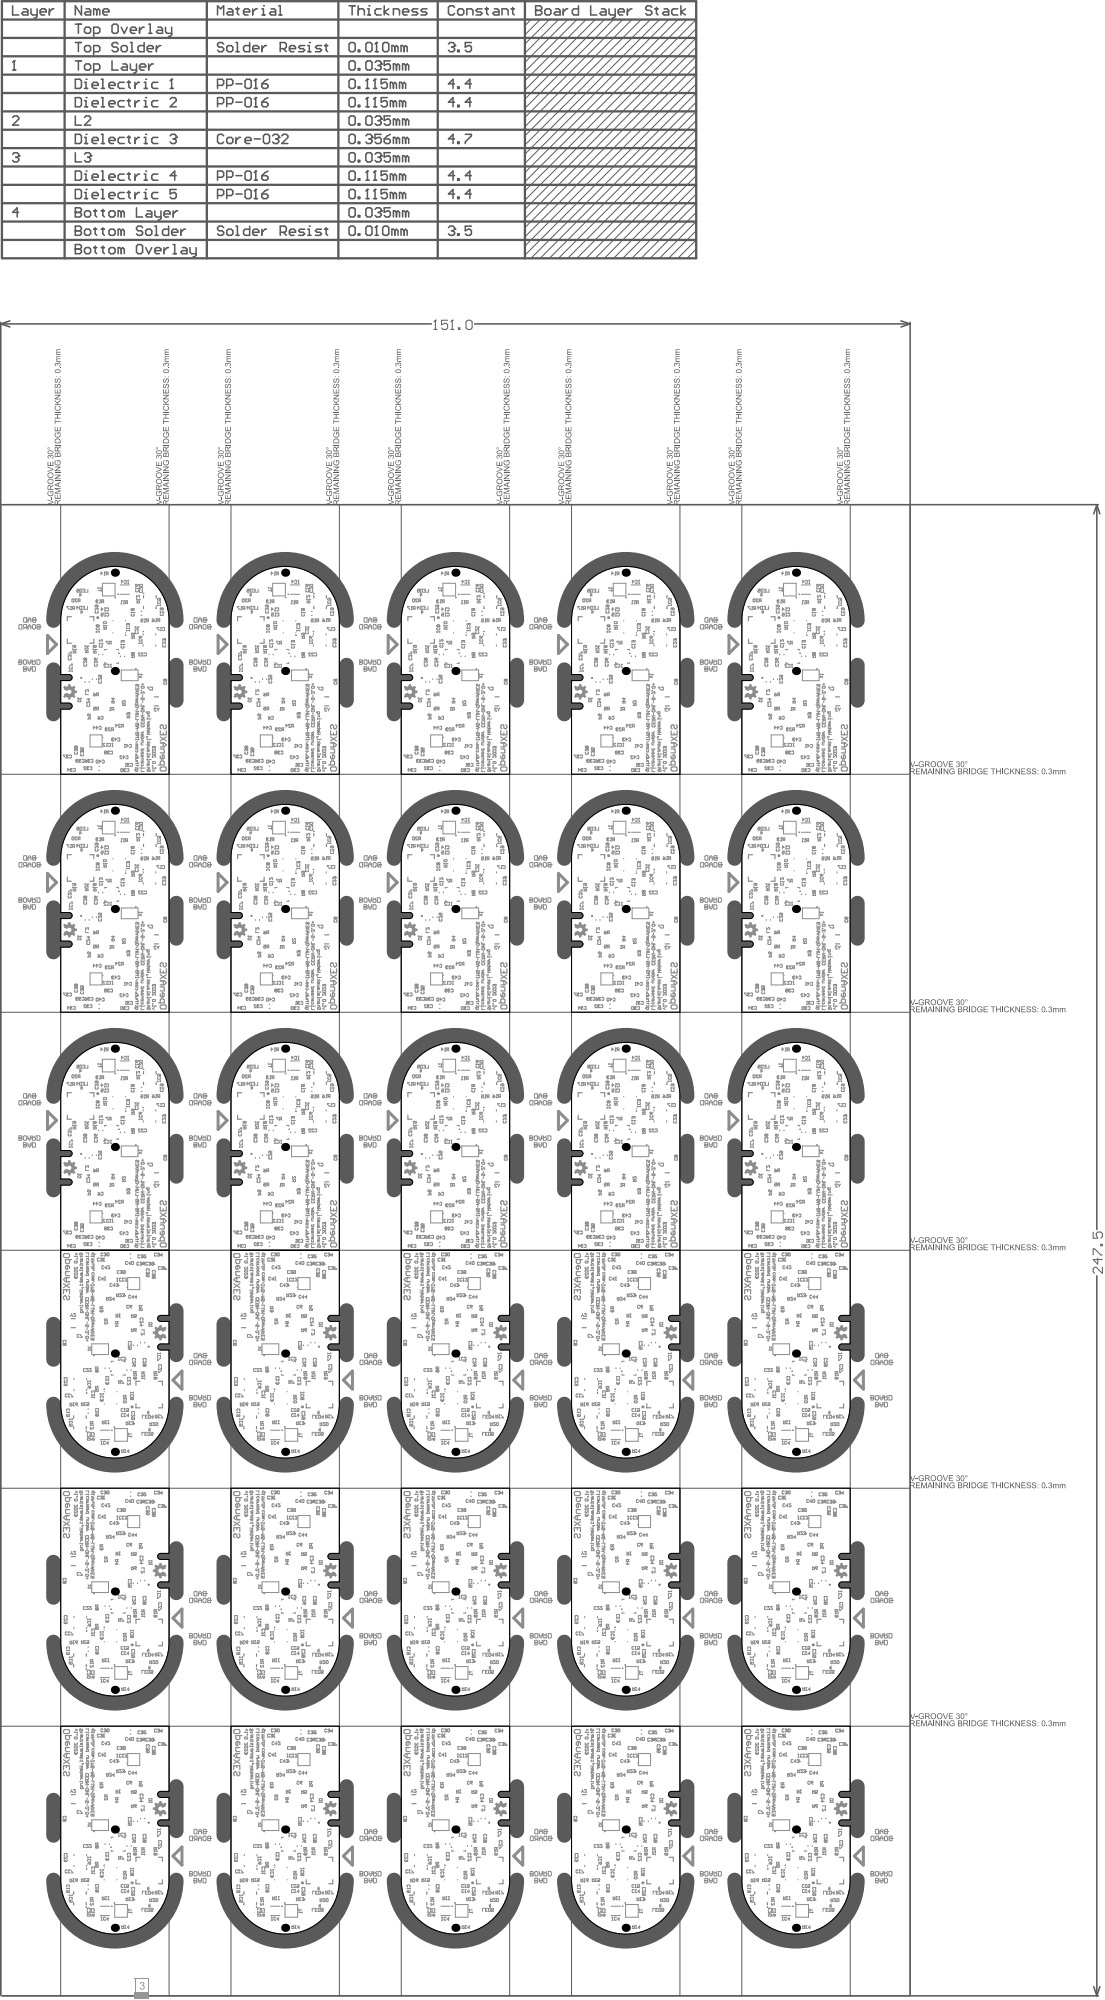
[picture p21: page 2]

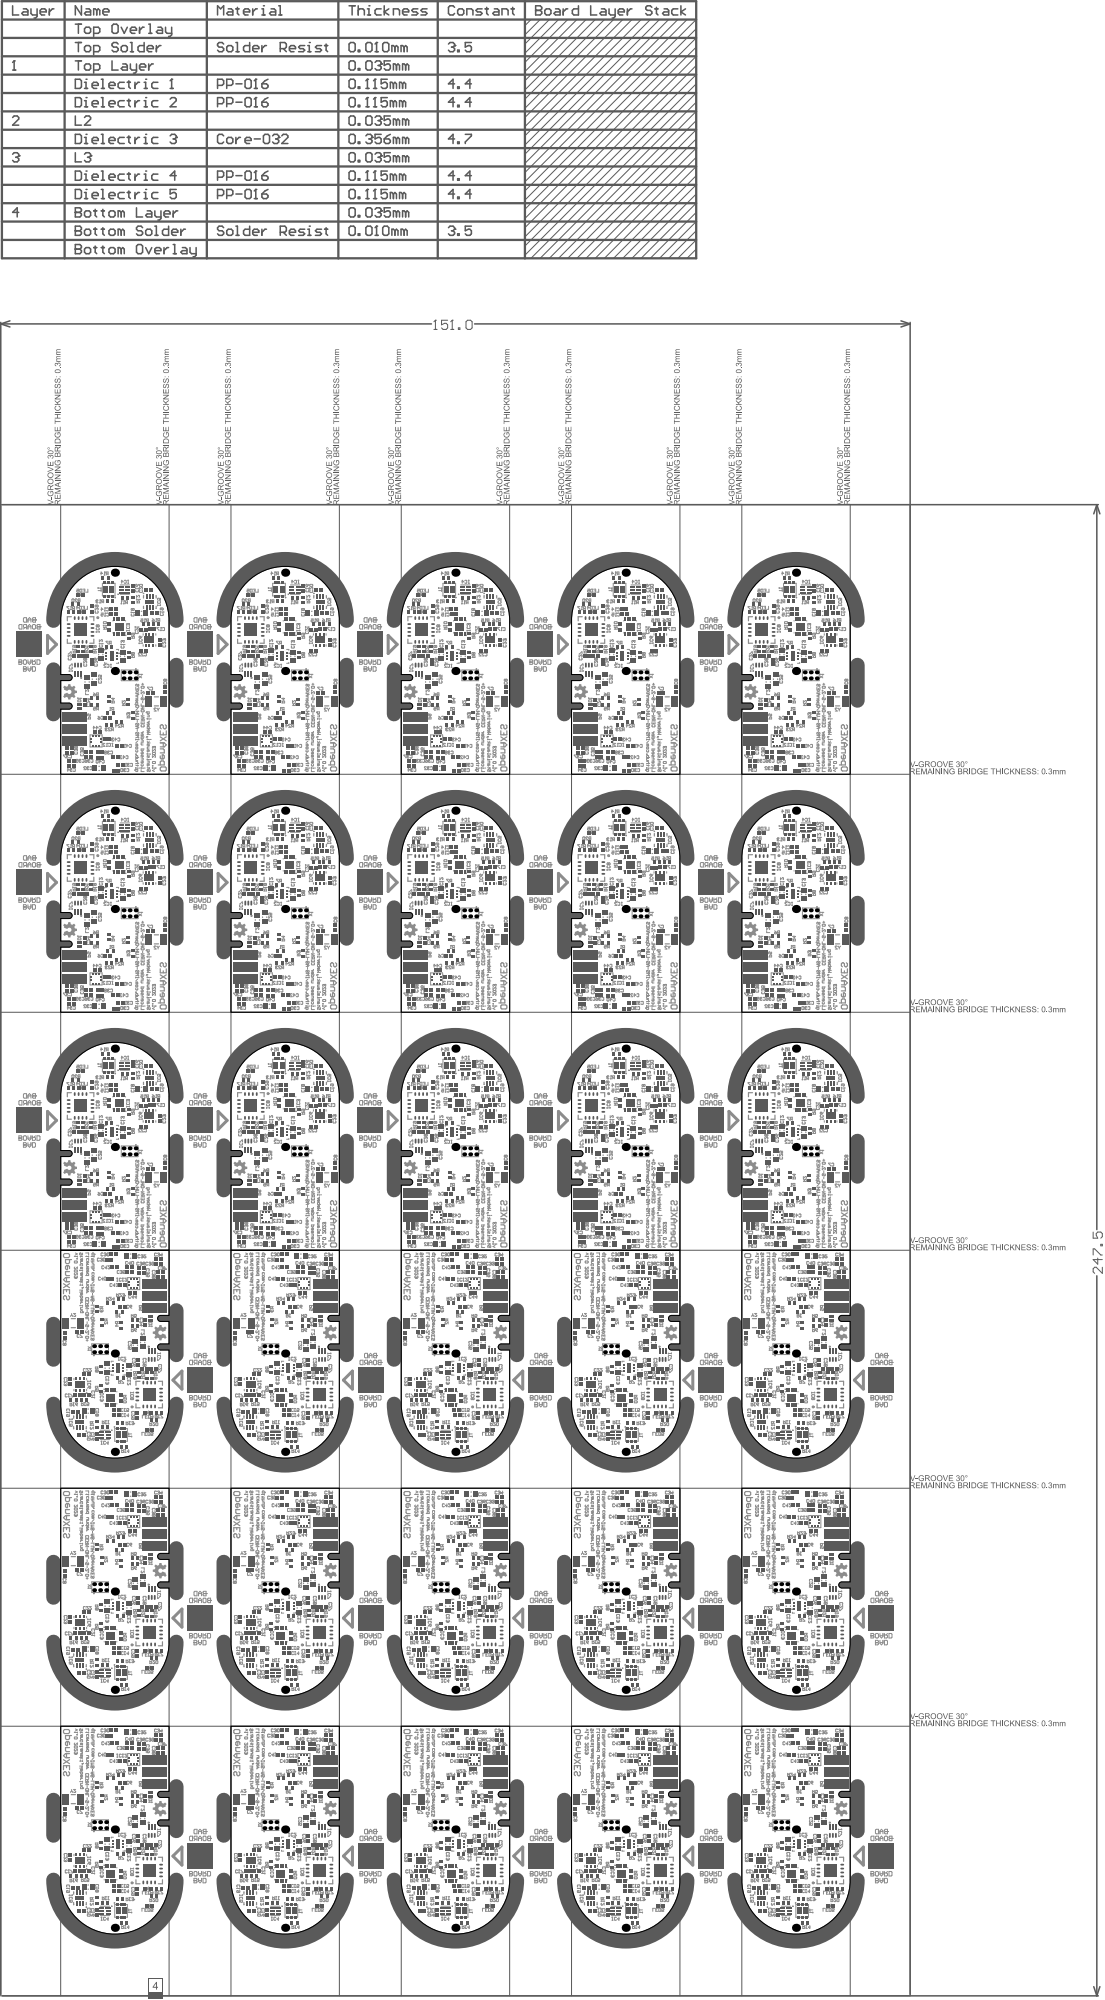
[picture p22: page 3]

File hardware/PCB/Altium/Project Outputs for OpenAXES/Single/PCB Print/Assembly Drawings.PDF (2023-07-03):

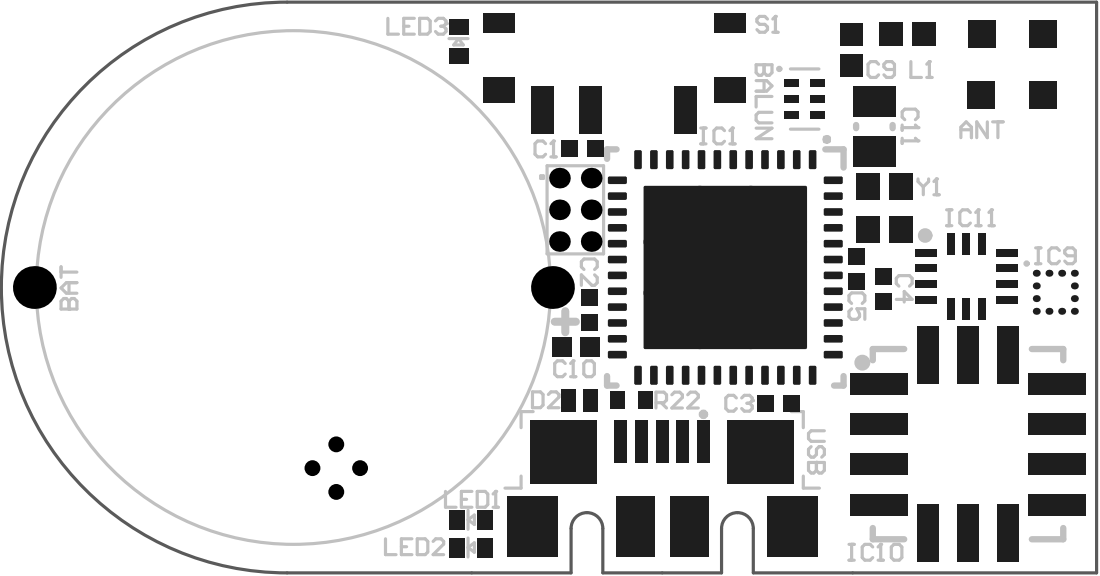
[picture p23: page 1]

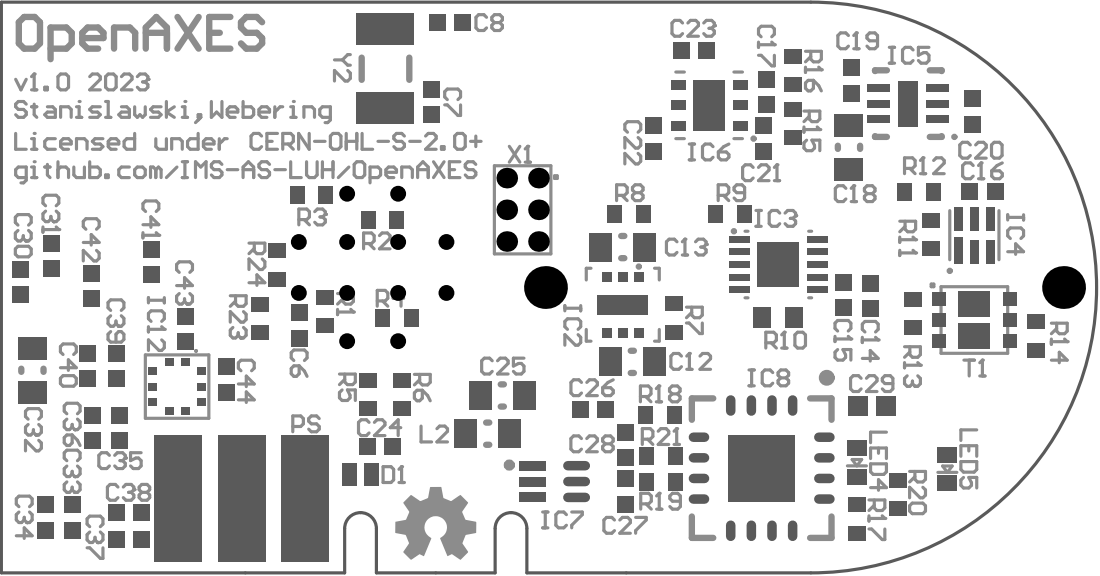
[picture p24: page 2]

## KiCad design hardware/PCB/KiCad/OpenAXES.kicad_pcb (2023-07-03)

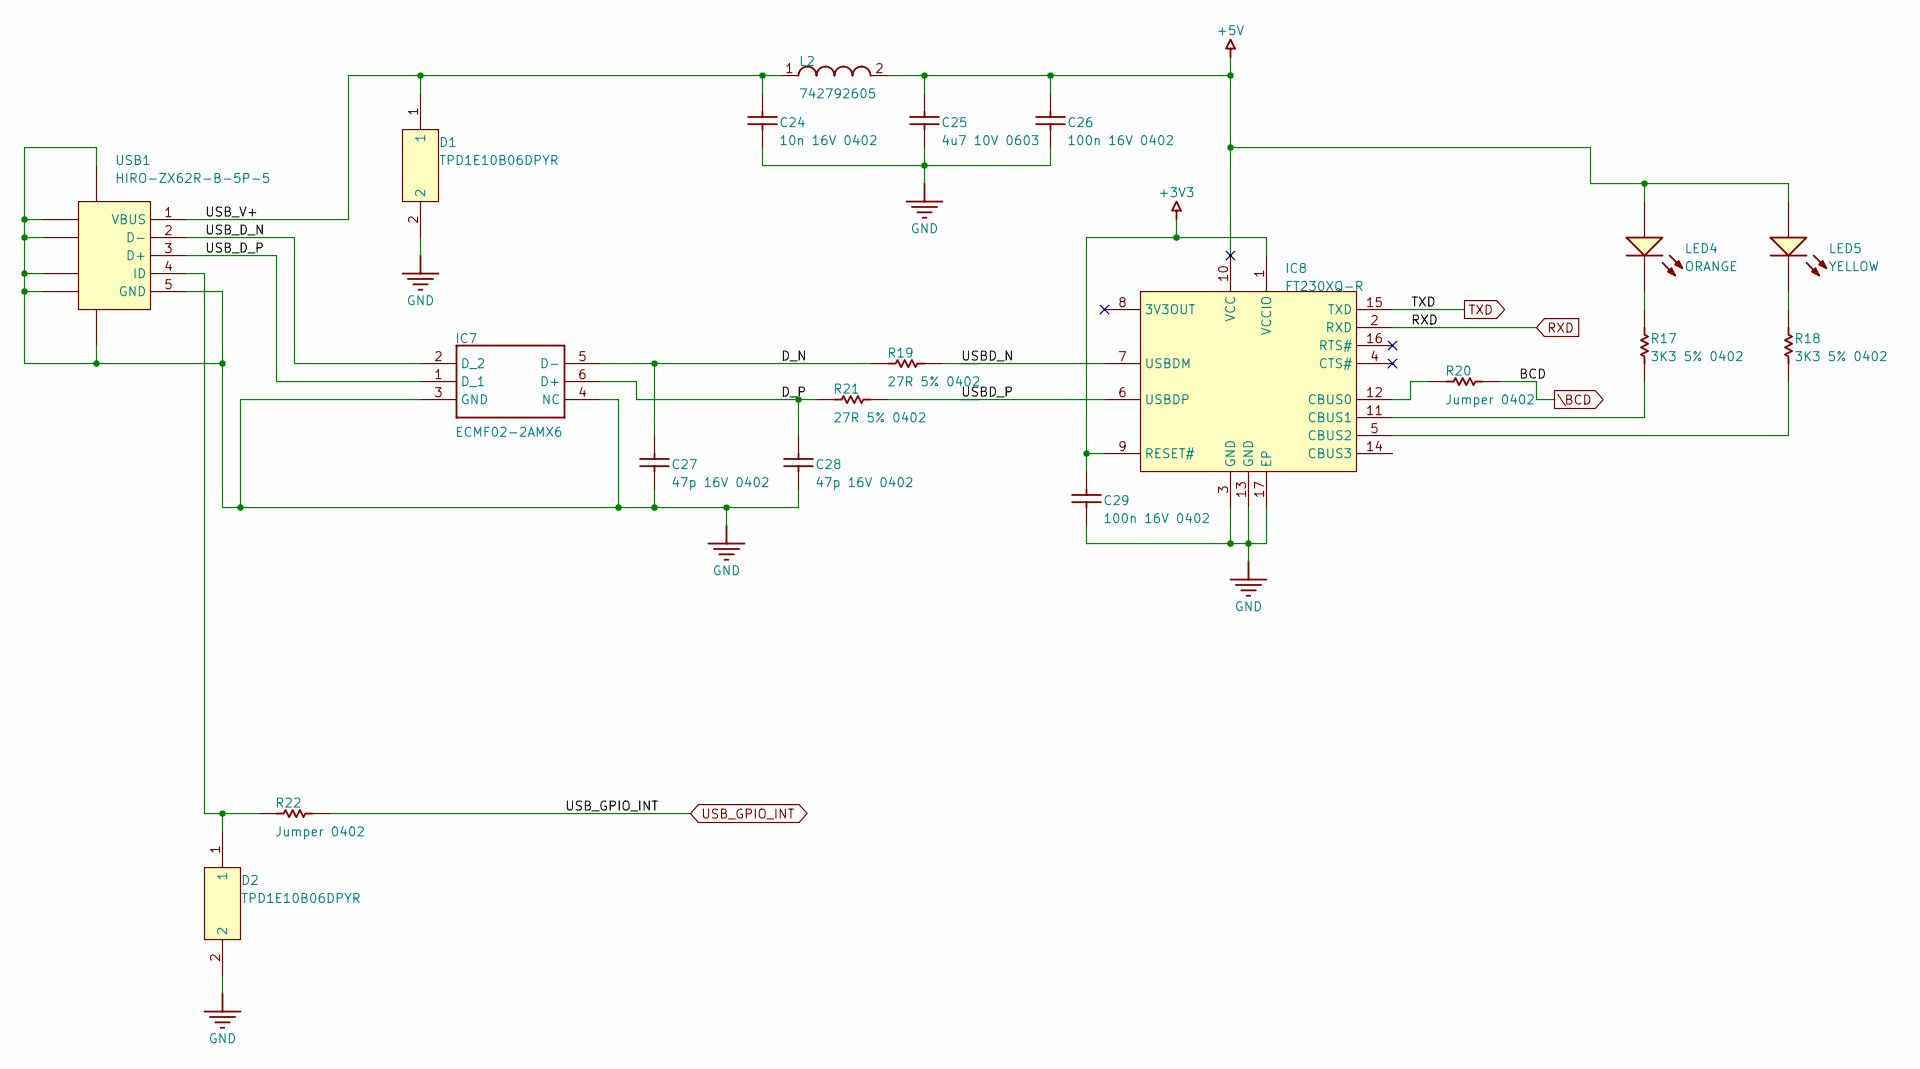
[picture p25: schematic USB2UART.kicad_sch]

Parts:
C24: 10n 16V 0402; CAPC0402(1005)33_L; TOLERANCE Â±10%; RATED VOLTAGE 16 V
C25: 4u7 10V 0603; CAPC0603(1608)100_L; TOLERANCE Â±20%; RATED VOLTAGE 10 V
C26: 100n 16V 0402; CAPC0402(1005)60_L; TOLERANCE Â±10%; RATED VOLTAGE 16 V
C27, C28: 47p 16V 0402; CAPC0402(1005)60_L; RATED VOLTAGE 16 V; TOLERANCE Â±10%
C29: 100n 16V 0402; CAPC0402(1005)60_N; TOLERANCE Â±10%; RATED VOLTAGE 16 V
D1, D2: TPD1E10B06DPYR; DPY0002A_M; BREAKDOWN VOLTAGE(MIN)(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 6; PARTNUMBER TPD1E10B06DPYR
IC7: ECMF02-2AMX6; SON50P150X170X55-6N-D; MANUFACTURER_PART_NUMBER ECMF02-2AMX6; MOUSER PART NUMBER 511-ECMF02-2AMX6
IC8: FT230XQ-R; QFN-16_L; PARTNUMBER FT230XQ-R
L2: 742792605; 0603(1608)_L
LED4: ORANGE; LED_0402
LED5: YELLOW; LED_0402
R17, R18: 3K3 5% 0402; RESC0402(1005)_L; TOLERANCE 5 %
R19, R21: 27R 5% 0402; RESC0402(1005)_L; TOLERANCE 5 %
R20, R22: Jumper 0402; RESC0402(1005)_L; TOLERANCE None
USB1: HIRO-ZX62R-B-5P-5; HIRO-ZX62R-B-5P_V

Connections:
+3V3: C29.2, IC8.1 (VCCIO), IC8.9 (RESET#); also elsewhere on the board
+5V: C25.2, C26.2, IC8.10 (VCC), L2.2, LED4.ANODE, LED5.ANODE; also elsewhere on the board
/USB2UART/D_N: C27.2, IC7.5 (D-), R19.1
/USB2UART/D_P: C28.2, IC7.6 (D+), R21.1
/USB2UART/USBD_N: IC8.7 (USBDM), R19.2
/USB2UART/USBD_P: IC8.6 (USBDP), R21.2
/USB2UART/USB_D_N: IC7.2 (D_2), USB1.2 (D-)
/USB2UART/USB_D_P: IC7.1 (D_1), USB1.3 (D+)
/USB2UART/USB_V+: C24.2, D1.1, L2.1, USB1.1 (VBUS)
GND: C24.1, C25.1, C26.1, C27.1, C28.1, C29.1, D1.2, D2.2, IC7.3 (GND), IC7.4 (NC), IC8.3 (GND), IC8.13 (GND), IC8.17 (EP), USB1.5 (GND), USB1.6 (SHLD), USB1.7 (SHLD), USB1.8 (SHLD), USB1.9 (SHLD), USB1.10 (SHLD), USB1.11 (SHLD); also elsewhere on the board
unnamed: IC8.12 (CBUS0), R20.1
unnamed: IC8.11 (CBUS1), R17.1
unnamed: IC8.5 (CBUS2), R18.1
unnamed: LED4.CATHODE, R17.2
unnamed: LED5.CATHODE, R18.2
unnamed: D2.1, R22.1, USB1.4 (ID)
RXD: IC8.2 (RXD); also elsewhere on the board
TXD: IC8.15 (TXD); also elsewhere on the board
USB_GPIO_INT: R22.2; also elsewhere on the board
\BCD: R20.2; also elsewhere on the board

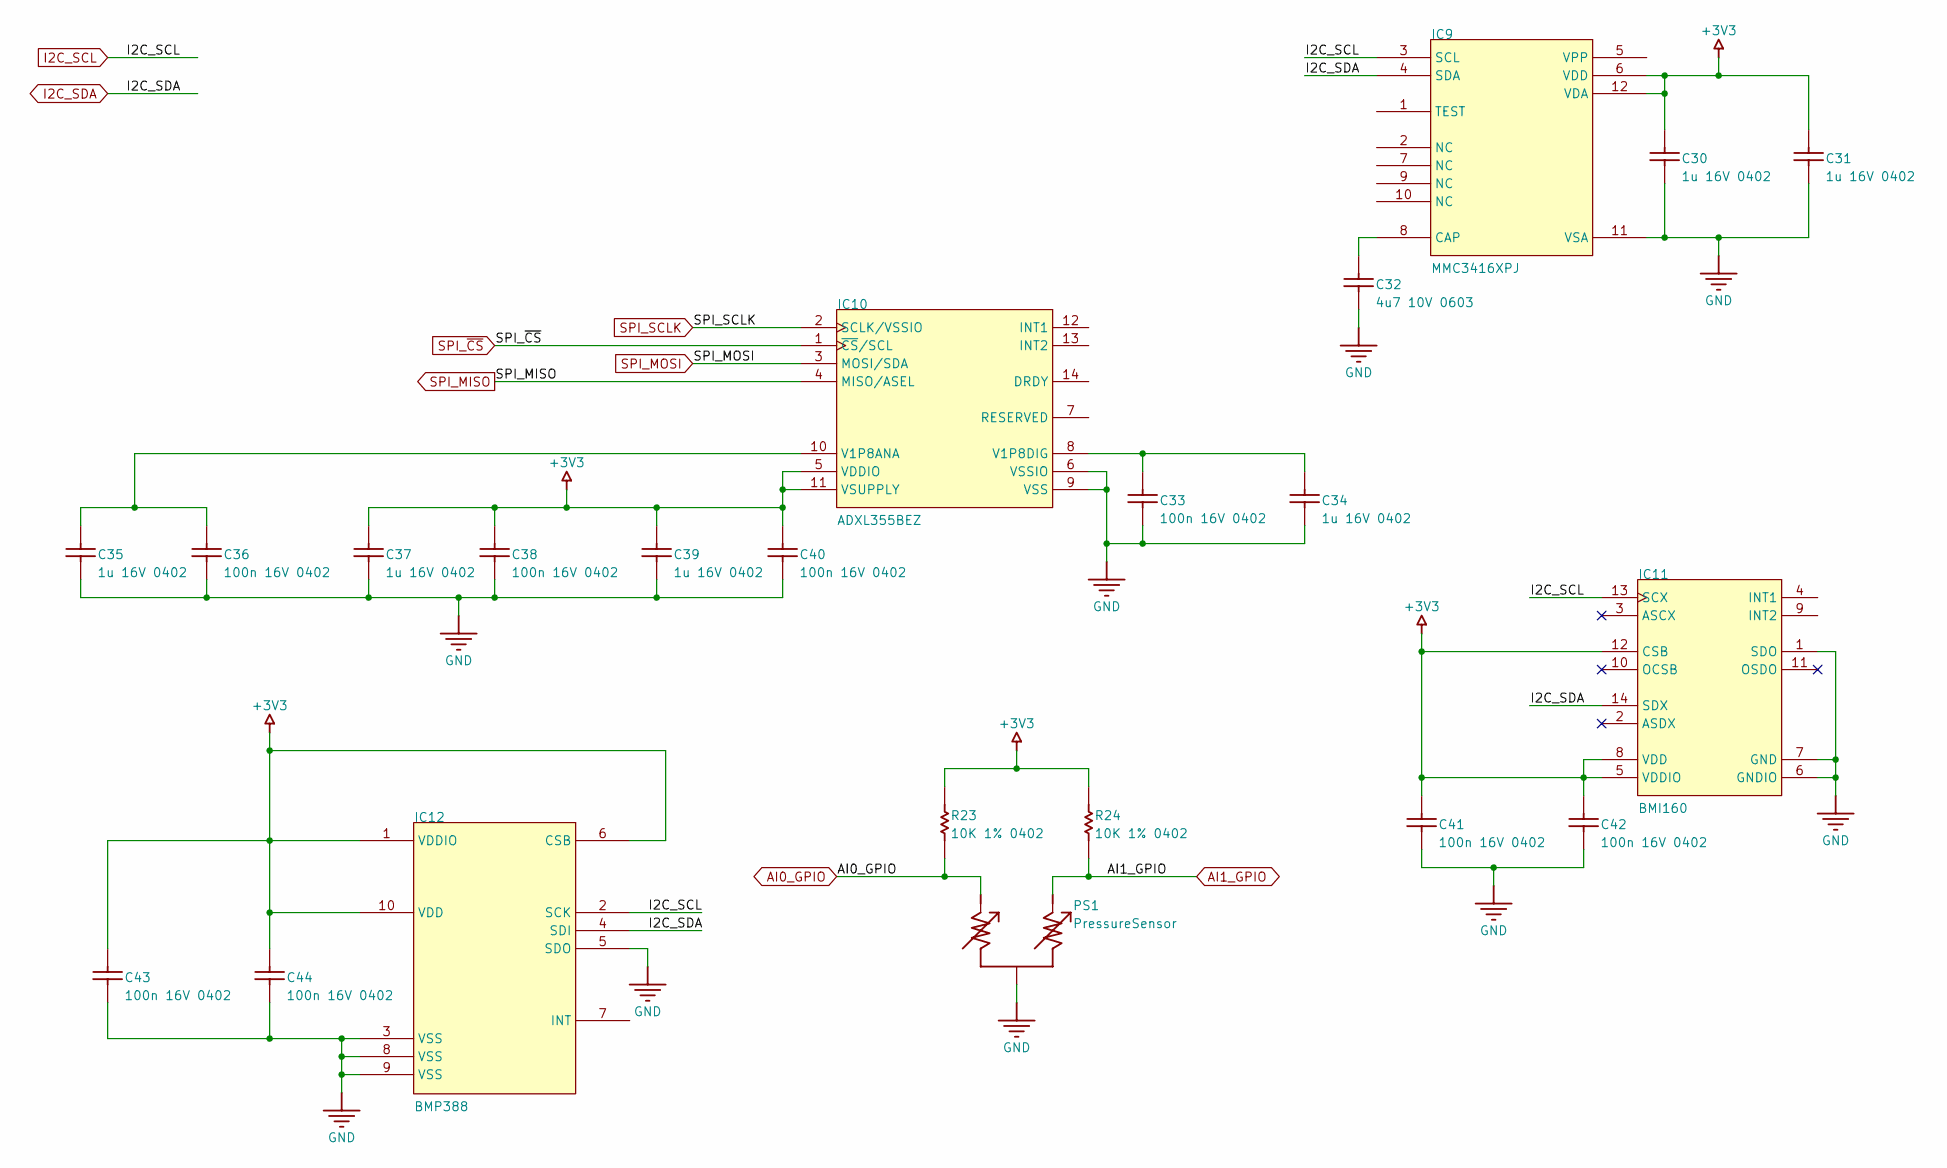
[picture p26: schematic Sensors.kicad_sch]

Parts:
C30, C31, C34, C35, C37, C39: 1u 16V 0402; CAPC0402(1005)60_L; RATED VOLTAGE 16 V; TOLERANCE Â±10%
C32: 4u7 10V 0603; CAPC0603(1608)100_L; TOLERANCE Â±20%; RATED VOLTAGE 10 V
C33, C36, C38, C40, C41, C42, C43, C44: 100n 16V 0402; CAPC0402(1005)60_L; TOLERANCE Â±10%; RATED VOLTAGE 16 V
IC9: MMC3416XPJ; BGA12C40P4X4_160X160X72
IC10: ADXL355BEZ; ADI-ADXL355-LCC-14_V
IC11: BMI160; BOSC-BMI160_V
IC12: BMP388
PS1: PressureSensor; PRESSURESENSOR
R23, R24: 10K 1% 0402; RESC0402(1005)_L; TOLERANCE 1 %

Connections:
+3V3: C30.1, C31.1, C37.1, C38.2, C39.1, C40.2, C41.2, C42.2, C43.2, C44.2, IC9.6 (VDD), IC9.12 (VDA), IC10.5 (VDDIO), IC10.11 (VSUPPLY), IC11.5 (VDDIO), IC11.8 (VDD), IC11.12 (CSB), IC12.1 (VDDIO), IC12.6 (CSB), IC12.10 (VDD), R23.2, R24.2; also elsewhere on the board
AI0_GPIO: PS1.3, R23.1; also elsewhere on the board
AI1_GPIO: PS1.2, R24.1; also elsewhere on the board
GND: C30.2, C31.2, C32.1, C33.1, C34.2, C35.2, C36.1, C37.2, C38.1, C39.2, C40.1, C41.1, C42.1, C43.1, C44.1, IC9.11 (VSA), IC10.6 (VSSIO), IC10.9 (VSS), IC11.1 (SDO), IC11.6 (GNDIO), IC11.7 (GND), IC12.3 (VSS), IC12.5 (SDO), IC12.8 (VSS), IC12.9 (VSS), PS1.1 (24); also elsewhere on the board
I2C_SCL: IC9.3 (SCL), IC11.13 (SCX), IC12.2 (SCK); also elsewhere on the board
I2C_SDA: IC9.4 (SDA), IC11.14 (SDX), IC12.4 (SDI); also elsewhere on the board
unnamed: C32.2, IC9.8 (CAP)
unnamed: C35.1, C36.2, IC10.10 (V1P8ANA)
unnamed: C33.2, C34.1, IC10.8 (V1P8DIG)
SPI_MISO: IC10.4 (MISO/ASEL); also elsewhere on the board
SPI_MOSI: IC10.3 (MOSI/SDA); also elsewhere on the board
SPI_SCLK: IC10.2 (SCLK/VSSIO); also elsewhere on the board
SPI_~CS: IC10.1 (~CS/SCL); also elsewhere on the board

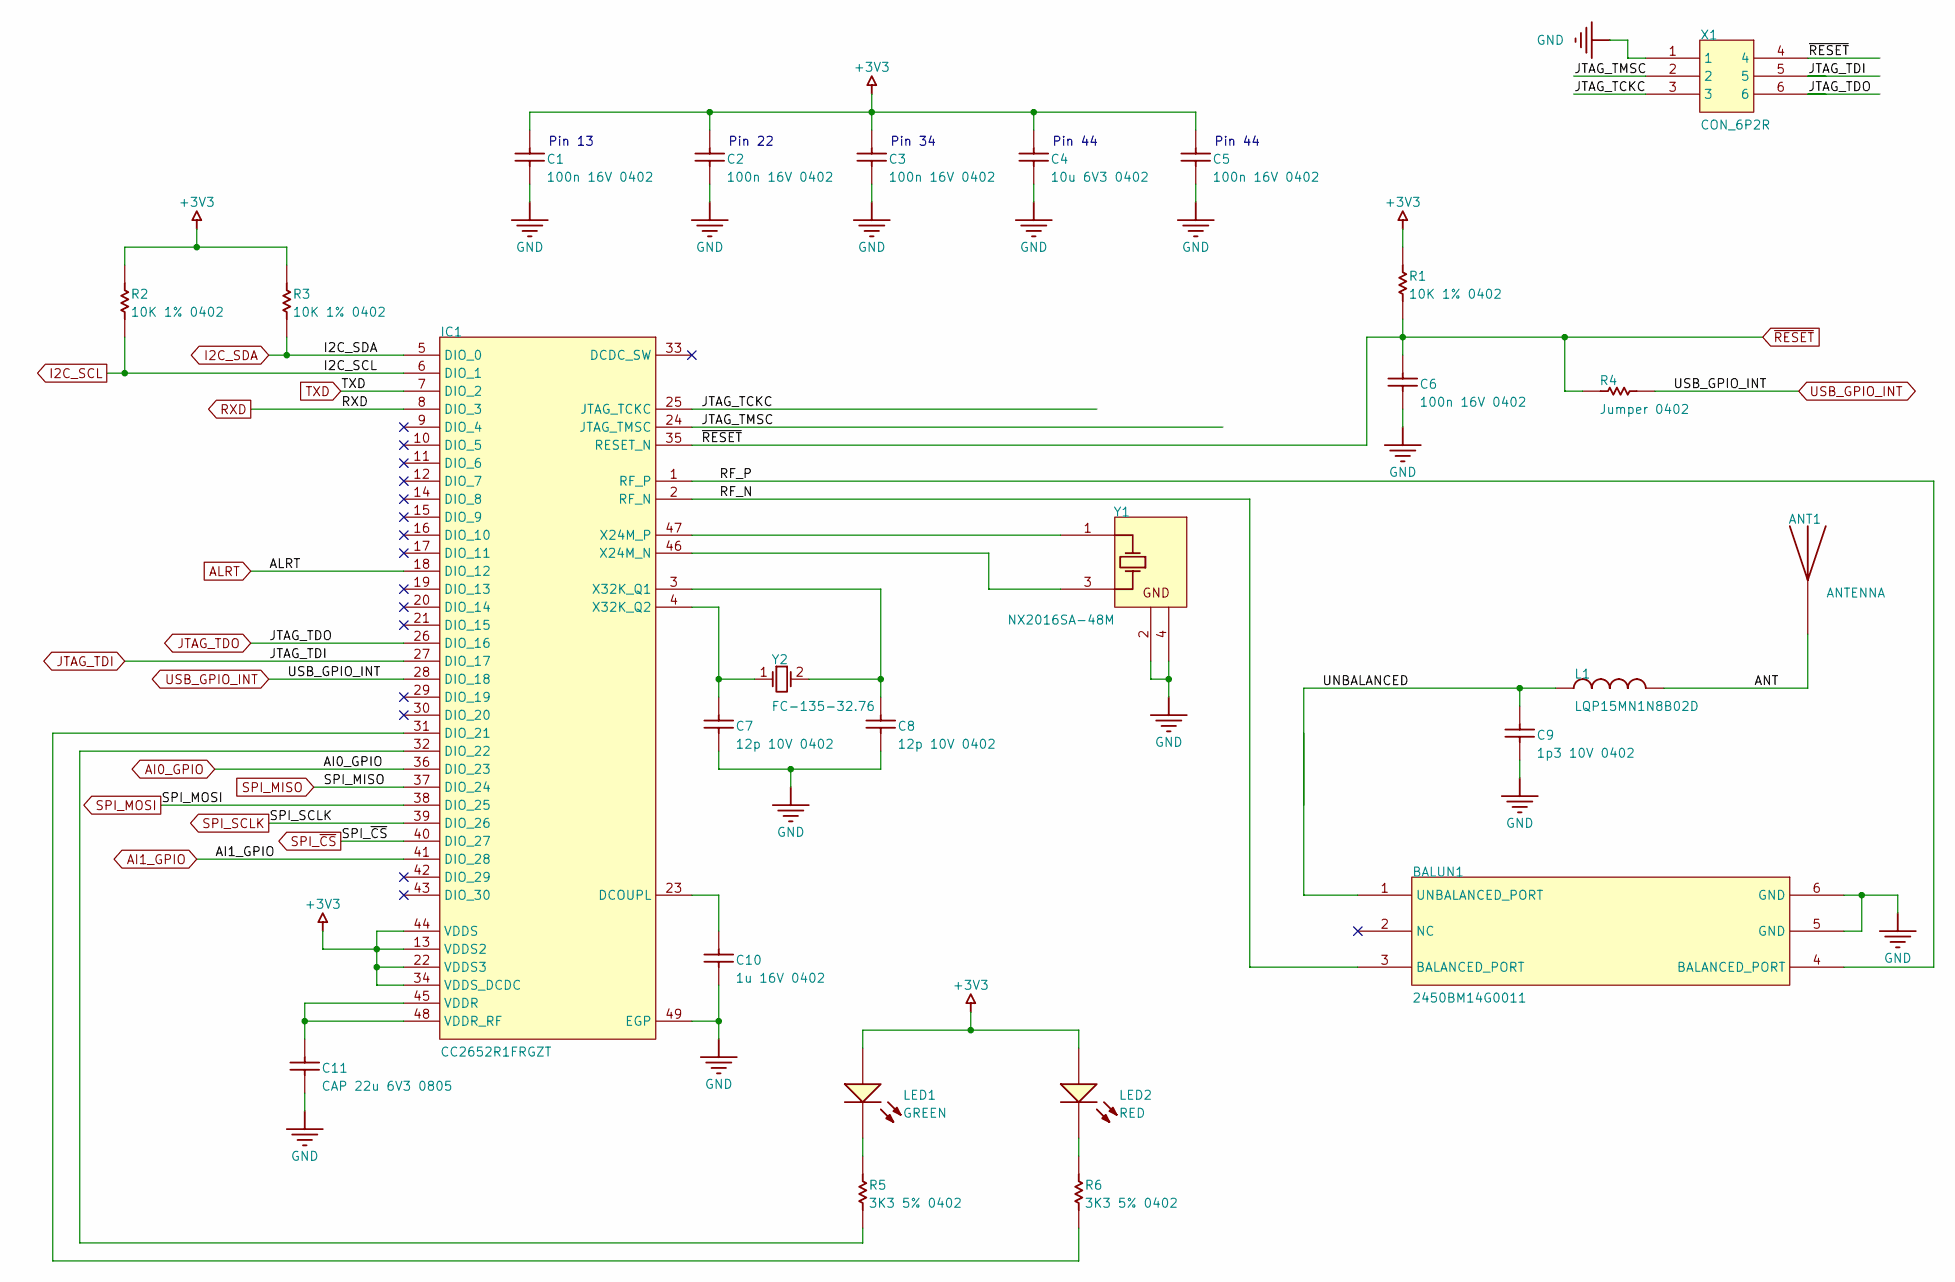
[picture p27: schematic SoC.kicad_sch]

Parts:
ANT1: ANTENNA; MOLEX_47948-0001
BALUN1: 2450BM14G0011; SON50P80X70-6L
C1, C2, C3, C5, C6: 100n 16V 0402; CAPC0402(1005)60_L; TOLERANCE Â±10%; RATED VOLTAGE 16 V
C4: 10u 6V3 0402; CAPC0402(1005)60_L; TOLERANCE Â±20%; RATED VOLTAGE 6.3 V
C7, C8: 12p 10V 0402; CAPC0402(1005)60_L; TOLERANCE Â±1%; RATED VOLTAGE 10 V
C9: 1p3 10V 0402; CAPC0402(1005)60_M; RATED VOLTAGE 10 V; TOLERANCE Â±0.25pF
C10: 1u 16V 0402; CAPC0402(1005)60_N; RATED VOLTAGE 16 V; TOLERANCE Â±10%
C11: CAP 22u 6V3 0805; CAPC0805(2012)145_L; RATED VOLTAGE 6.3 V; TOLERANCE Â±10%
IC1: CC2652R1FRGZT; RGZ0048A_V
L1: LQP15MN1N8B02D; INDC1005X45X25ML10T10; TOLERANCE (NH) ±0.1nH
LED1: GREEN; LED_0402
LED2: RED; LED_0402
R1, R2, R3: 10K 1% 0402; RESC0402(1005)_L; TOLERANCE 1 %
R4: Jumper 0402; RESC0402(1005)_L; TOLERANCE None
R5, R6: 3K3 5% 0402; RESC0402(1005)_L; TOLERANCE 5 %
X1: CON_6P2R; JTAG_CON
Y1: NX2016SA-48M; Crystal_2016
Y2: FC-135-32.76; EPSON-FC-135_V

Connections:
+3V3: C1.2, C2.2, C3.2, C4.2, C5.2, IC1.13 (VDDS2), IC1.22 (VDDS3), IC1.34 (VDDS_DCDC), IC1.44 (VDDS), LED1.ANODE, LED2.ANODE, R1.2, R2.2, R3.2; also elsewhere on the board
/SoC/ANT: ANT1.ANTENNA (23), L1.2
/SoC/JTAG_TCKC: IC1.25 (JTAG_TCKC), X1.3
/SoC/JTAG_TMSC: IC1.24 (JTAG_TMSC), X1.2
/SoC/RF_N: BALUN1.3 (BALANCED_PORT), IC1.2 (RF_N)
/SoC/RF_P: BALUN1.4 (BALANCED_PORT), IC1.1 (RF_P)
/SoC/UNBALANCED: BALUN1.1 (UNBALANCED_PORT), C9.2, L1.1
AI0_GPIO: IC1.36 (DIO_23); also elsewhere on the board
AI1_GPIO: IC1.41 (DIO_28); also elsewhere on the board
ALRT: IC1.18 (DIO_12); also elsewhere on the board
GND: BALUN1.5 (GND), BALUN1.6 (GND), C1.1, C2.1, C3.1, C4.1, C5.1, C6.1, C7.1, C8.1, C9.1, C10.1, C11.1, IC1.49 (EGP), X1.1, Y1.2 (GND), Y1.4 (GND); also elsewhere on the board
I2C_SCL: IC1.6 (DIO_1), R2.1; also elsewhere on the board
I2C_SDA: IC1.5 (DIO_0), R3.1; also elsewhere on the board
JTAG_TDI: IC1.27 (DIO_17), X1.5
JTAG_TDO: IC1.26 (DIO_16), X1.6
unnamed: C10.2, IC1.23 (DCOUPL)
unnamed: IC1.31 (DIO_21), R6.1
unnamed: IC1.32 (DIO_22), R5.1
unnamed: C11.2, IC1.45 (VDDR), IC1.48 (VDDR_RF)
unnamed: IC1.46 (X24M_N), Y1.3 (X2)
unnamed: IC1.47 (X24M_P), Y1.1 (X1)
unnamed: C8.2, IC1.3 (X32K_Q1), Y2.2
unnamed: C7.2, IC1.4 (X32K_Q2), Y2.1
unnamed: LED1.CATHODE, R5.2
unnamed: LED2.CATHODE, R6.2
RXD: IC1.8 (DIO_3); also elsewhere on the board
SPI_MISO: IC1.37 (DIO_24); also elsewhere on the board
SPI_MOSI: IC1.38 (DIO_25); also elsewhere on the board
SPI_SCLK: IC1.39 (DIO_26); also elsewhere on the board
SPI_~CS: IC1.40 (DIO_27); also elsewhere on the board
TXD: IC1.7 (DIO_2); also elsewhere on the board
USB_GPIO_INT: IC1.28 (DIO_18), R4.2; also elsewhere on the board
~RESET: C6.2, IC1.35 (RESET_N), R1.1, R4.1, X1.4

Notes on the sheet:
Pin 44
Pin 34
Pin 13
Pin 22

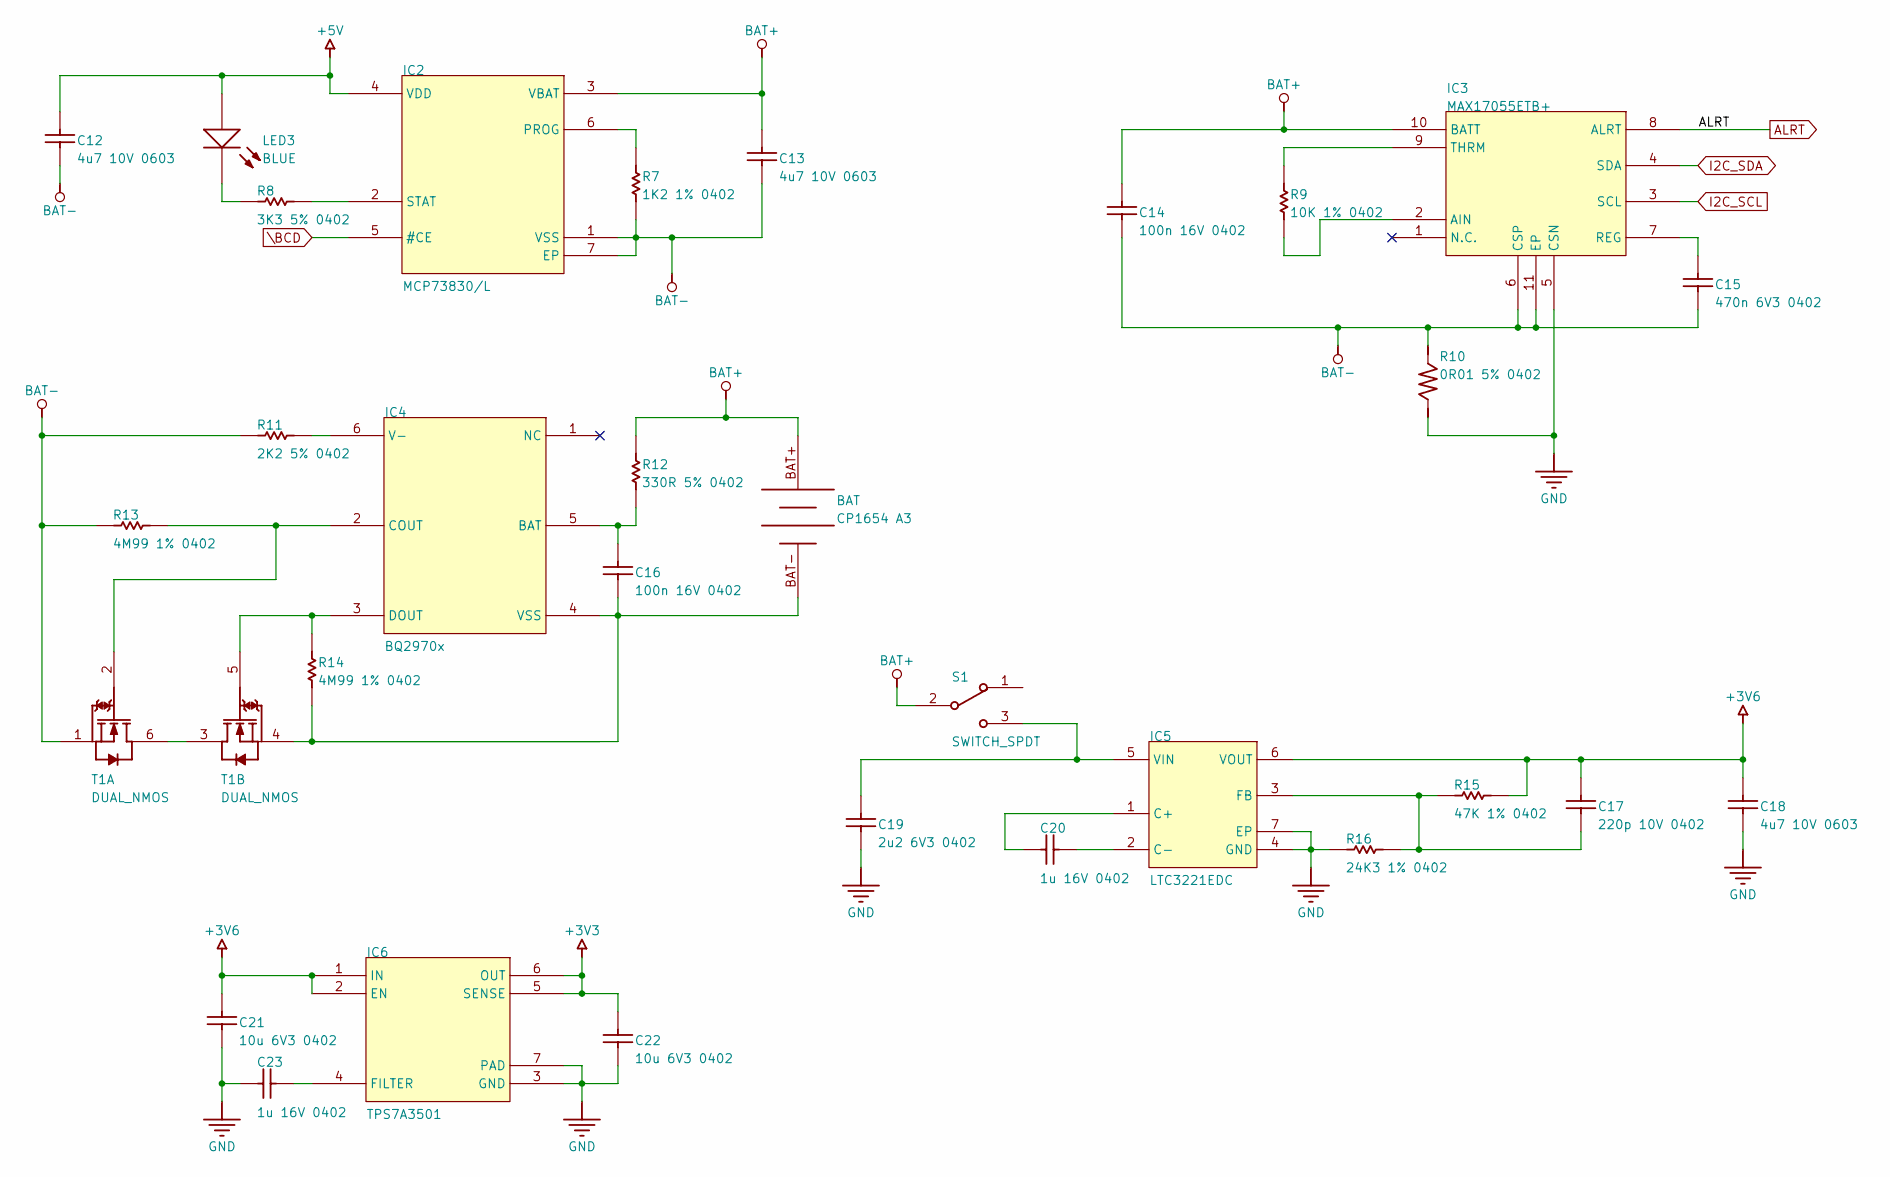
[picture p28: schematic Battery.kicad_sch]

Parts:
BAT: CP1654 A3; CP1654
C12, C13, C18: 4u7 10V 0603; CAPC0603(1608)100_L; TOLERANCE Â±20%; RATED VOLTAGE 10 V
C14, C16: 100n 16V 0402; CAPC0402(1005)60_L; TOLERANCE Â±10%; RATED VOLTAGE 16 V
C15: 470n 6V3 0402; CAPC0402(1005)60_L; RATED VOLTAGE 6.3 V; TOLERANCE Â±10%
C17: 220p 10V 0402; CAPC0402(1005)60_L; RATED VOLTAGE 10 V; TOLERANCE Â±5%
C19: 2u2 6V3 0402; CAPC0402(1005)60_L; RATED VOLTAGE 6.3 V; TOLERANCE Â±10%
C20, C23: 1u 16V 0402; CAPC0402(1005)60_L; RATED VOLTAGE 16 V; TOLERANCE Â±10%
C21, C22: 10u 6V3 0402; CAPC0402(1005)60_L; TOLERANCE Â±20%; RATED VOLTAGE 6.3 V
IC2: MCP73830/L; PSON50P200X80_HS-7L
IC3: MAX17055ETB+; PSON40P250X80_HS-11L
IC4: BQ2970x; SON50P150X80-6L
IC5: LTC3221EDC; LT-DC6-6_V; PARTNUMBER LTC3221EDC
IC6: TPS7A3501; PSON65P200X80_HS-7L
LED3: BLUE; LED_0402
R7: 1K2 1% 0402; RESC0402(1005)_L; TOLERANCE 1 %
R8: 3K3 5% 0402; RESC0402(1005)_L; TOLERANCE 5 %
R9: 10K 1% 0402; RESC0402(1005)_L; TOLERANCE 1 %
R10: 0R01 5% 0402; R0402
R11: 2K2 5% 0402; RESC0402(1005)_L; TOLERANCE 5 %
R12: 330R 5% 0402; RESC0402(1005)_L; TOLERANCE 5 %
R13, R14: 4M99 1% 0402; RESC0402(1005)_L; TOLERANCE 1 %
R15: 47K 1% 0402; RESC0402(1005)_L; TOLERANCE 1 %
R16: 24K3 1% 0402; RESC0402(1005)_L; TOLERANCE 1 %
S1: SWITCH_SPDT; SSSS810701_MODIFIED
T1: DUAL_NMOS; WDFN6 2X2 0.65P

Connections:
+3V3: C22.2, IC6.5 (SENSE), IC6.6 (OUT); also elsewhere on the board
+3V6: C17.2, C18.2, C21.2, IC5.6 (VOUT), IC6.1 (IN), IC6.2 (EN), R15.2
+5V: C12.2, IC2.4 (VDD), LED3.ANODE; also elsewhere on the board
ALRT: IC3.8 (ALRT); also elsewhere on the board
BAT+: C13.2, C14.2, IC2.3 (VBAT), IC3.10 (BATT), R12.2, S1.2; also elsewhere on the board
BAT-: C12.1, C13.1, C14.1, C15.1, IC2.1 (VSS), IC2.7 (EP), IC3.6 (CSP), IC3.11 (EP), R7.1, R10.1 (24), R11.1, R13.1, T1.1 (S1)
GND: C18.1, C19.1, C21.1, C22.1, C23.2, IC3.5 (CSN), IC5.4 (GND), IC5.7 (EP), IC6.3 (GND), IC6.7 (PAD), R10.2, R16.1; also elsewhere on the board
I2C_SCL: IC3.3 (SCL); also elsewhere on the board
I2C_SDA: IC3.4 (SDA); also elsewhere on the board
unnamed: IC2.6 (PROG), R7.2
unnamed: IC2.2 (STAT), R8.2
unnamed: IC3.2 (AIN), R9.1
unnamed: C15.2, IC3.7 (REG)
unnamed: IC3.9 (THRM), R9.2
unnamed: C16.2, IC4.5 (BAT), R12.1
unnamed: IC4.2 (COUT), R13.2, T1.2 (G1)
unnamed: IC4.3 (DOUT), R14.2, T1.5 (G2)
unnamed: IC4.6 (V-), R11.2
unnamed 43: C16.1, IC4.4 (VSS), R14.1, T1.4 (S2); also elsewhere on the board
unnamed: C20.2, IC5.1 (C+)
unnamed: C20.1, IC5.2 (C-)
unnamed: C17.1, IC5.3 (FB), R15.1, R16.2
unnamed: C19.2, IC5.5 (VIN), S1.3
unnamed: C23.1, IC6.4 (FILTER)
unnamed: LED3.CATHODE, R8.1
unnamed: T1.3 (D2), T1.6 (D1)
\BCD: IC2.5 (#CE); also elsewhere on the board

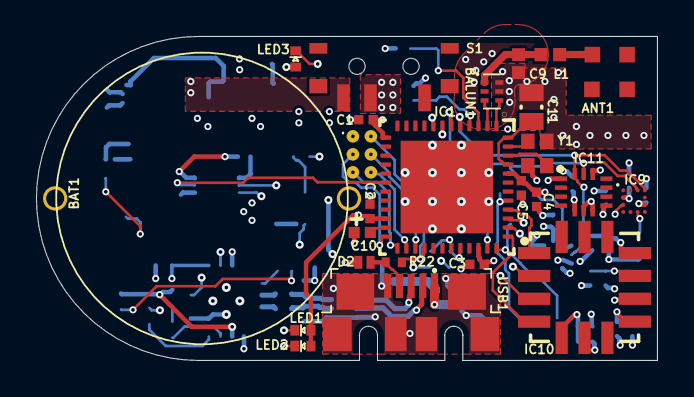
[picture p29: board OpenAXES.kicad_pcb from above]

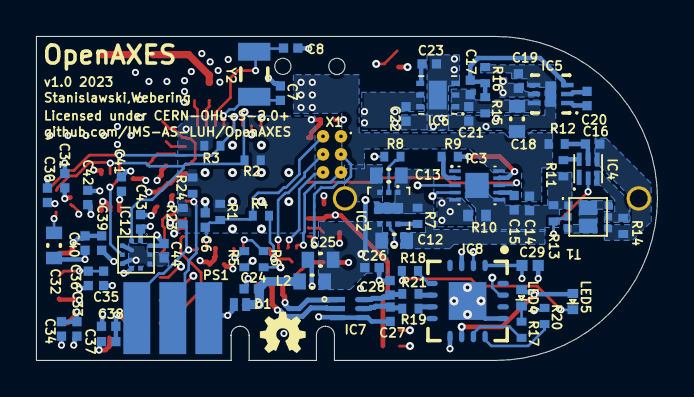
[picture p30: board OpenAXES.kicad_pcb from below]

Board: 4 copper layers, 34.5 x 18.0 mm, 99 parts (74 on the bottom side), 71 nets.

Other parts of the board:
BAT1: CP1654 A3; CP1654

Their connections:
BAT+: BAT1.BAT+; also elsewhere on the board
unnamed 43: BAT1.BAT-; also elsewhere on the board

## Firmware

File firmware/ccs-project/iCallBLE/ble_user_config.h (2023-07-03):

/******************************************************************************
 @file:       ble_user_config.h

 @brief:    This file contains user configurable variables for the BLE
            Controller and Host. This file is also used for defining the
            type of RF Front End used with the TI device, such as using
            a Differential front end with External Bias, etc. Please see
            below for more detail.

            To change the default values of configurable variables:
              - Include the followings in your application main.c file:
                #ifndef USE_DEFAULT_USER_CFG

                #include "ble_user_config.h"

                // BLE user defined configuration
                bleUserCfg_t user0Cfg = BLE_USER_CFG;

                #endif // USE_DEFAULT_USER_CFG
              - Set the preprocessor symbol MAX_NUM_BLE_CONNS, MAX_NUM_PDU,
                MAX_PDU_SIZE, L2CAP_NUM_PSM or L2CAP_NUM_CO_CHANNELS
                to a desired value in your application project.
              - Include "ble_user_config.h" in your stack OSAL_ICallBle.c
                file.
              - Call setBleUserConfig at the start of stack_main. Actually,
                it is okay to set the variables anywhere in stack_main as
                long as it is BEFORE osal_init_system, but best to set at
                the very start of stack_main.

            Note: User configurable variables are only used during the
                  initialization of the Controller and Host. Changing
                  the values of these variables after this will have no
                  effect.

            Note: To use the default user configurable variables, define
                  the preprocessor symbol USE_DEFAULT_USER_CFG in your
                  application project.

            For example:
              - In your application main.c, include:
                #ifndef USE_DEFAULT_USER_CFG

                #include "bleUserConfig.h"

                // BLE user defined configuration
                bleUserCfg_t user0Cfg = BLE_USER_CFG;
                #endif // USE_DEFAULT_USER_CFG
              - In your application project, set the preprocessor symbol
                MAX_NUM_BLE_CONNS to 1 to change the maximum number of BLE
                connections to 1 from the default value of 3.
              - In your stack OSAL_ICallBle.c file, call setBleUserCfg to
                update the user configuration variables:
                #include "bleUserConfig.h"
                :
                int stack_main(void *arg)
                {
                  setBleUserConfig((bleUserCfg_t *)arg);
                  :
                }

            Default values:
              maxNumConns       : 1
              maxNumPDUs        : 5
              maxPduSize        : 27 (or 69 if Secure Connection enabled)
              maxNumPSM         : 3
              maxNumCoChannels  : 3
              maxWhiteListElems : 16
              maxResolvListElems: 10

 Group: WCS, BTS
 Target Device: cc13x2_26x2

 ******************************************************************************
 
 Copyright (c) 2014-2020, Texas Instruments Incorporated
 All rights reserved.

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
 *  Neither the name of Texas Instruments Incorporated nor the names of
    its contributors may be used to endorse or promote products derived
    from this software without specific prior written permission.

 THIS SOFTWARE IS PROVIDED BY THE COPYRIGHT HOLDERS AND CONTRIBUTORS "AS IS"
 AND ANY EXPRESS OR IMPLIED WARRANTIES, INCLUDING, BUT NOT LIMITED TO,
 THE IMPLIED WARRANTIES OF MERCHANTABILITY AND FITNESS FOR A PARTICULAR
 PURPOSE ARE DISCLAIMED. IN NO EVENT SHALL THE COPYRIGHT OWNER OR
 CONTRIBUTORS BE LIABLE FOR ANY DIRECT, INDIRECT, INCIDENTAL, SPECIAL,
 EXEMPLARY, OR CONSEQUENTIAL DAMAGES (INCLUDING, BUT NOT LIMITED TO,
 PROCUREMENT OF SUBSTITUTE GOODS OR SERVICES; LOSS OF USE, DATA, OR PROFITS;
 OR BUSINESS INTERRUPTION) HOWEVER CAUSED AND ON ANY THEORY OF LIABILITY,
 WHETHER IN CONTRACT, STRICT LIABILITY, OR TORT (INCLUDING NEGLIGENCE OR
 OTHERWISE) ARISING IN ANY WAY OUT OF THE USE OF THIS SOFTWARE,
 EVEN IF ADVISED OF THE POSSIBILITY OF SUCH DAMAGE.

 ******************************************************************************
 
 
 *****************************************************************************/
#ifndef BLE_USER_CONFIG_H
#define BLE_USER_CONFIG_H

#ifdef __cplusplus
extern "C"
{
#endif

/*******************************************************************************
 * INCLUDES
 */

#ifdef ICALL_JT
#include "icall_user_config.h"
#include <ti/drivers/rf/RF.h>
#endif /* ICALL_JT */

#include "ble_dispatch.h"
#include "hal_assert.h"

#include "rf_hal.h"

/*******************************************************************************
 * MACROS
 */

//
// Tx Power
//
// PG1:              PG2:
// 7..6 | 5..0         15..8   | 7..6 | 5..0
//  GC  |  IB        tempCoeff |  GC  |  IB
//
#if defined(CC26X2) || defined(CC13X2)

#define GEN_TX_POWER_VAL(ib, gc, tc)                                            \
  (uint16)(((ib) & 0x3F) | (((gc) & 0x03) << 6) | (((tc)&0x7F) << 9))

#endif // CC26X2 || CC13X2

// taken from RF_TxPowerTable_DEFAULT_PA_ENTRY in RF.h
#define RF_TxPowerTable_DefaultPAEntry(bias, gain, boost, coefficient)          \
  (uint32)(((bias) << 0) | ((gain) << 6) | ((boost) << 8) | ((coefficient) << 9) | (RF_TxPowerTable_DefaultPA << 31))

#if defined(CC13X2P)

// taken from RF_TxPowerTable_HIGH_PA_ENTRY in RF.h
#define RF_TxPowerTable_HighPAEntry(bias, ibboost, boost, coefficient, ldotrim) \
  (uint32)(((bias) << 0) | ((ibboost) << 6) | ((boost) << 8) | ((coefficient) << 9) | ((ldotrim) << 16) | (RF_TxPowerTable_HighPA << 31))

#endif // CC13X2P

/*******************************************************************************
 * CONSTANTS
 */

// Defines only required by Application.
// Note: ICALL_STACK0_ADDR is assigned the entry point of the stack image and
//       is only defined for the Application project
#if defined(ICALL_STACK0_ADDR)

#include <ti_drivers_config.h>

// RF Front End Settings
// Note: The use of these values completely depends on how the PCB is laid out.
//       Please see Device Package and Evaluation Module (EM) Board below.
#define RF_FE_DIFFERENTIAL              0
#define RF_FE_SINGLE_ENDED_RFP          1
#define RF_FE_SINGLE_ENDED_RFN          2
#define RF_FE_ANT_DIVERSITY_RFP_FIRST   3
#define RF_FE_ANT_DIVERSITY_RFN_FIRST   4
#define RF_FE_SINGLE_ENDED_RFP_EXT_PINS 5
#define RF_FE_SINGLE_ENDED_RFN_EXT_PINS 6
//
#define RF_FE_INT_BIAS                  (0<<3)
#define RF_FE_EXT_BIAS                  (1<<3)

// This is a common file for the legacy and sysconfig examples,
// the parameters under ifndef SYSCFG are defined in this file for
// the legacy examples and generated using the sysconfig tool for
// the sysconfig examples
#ifndef SYSCFG
// Maximum number of BLE connections. It should be set based on the
// device GAP role. Here're some recommended values:
//      * Central:     3
//      * Peripheral:  1
//      * Observer:    0
//      * Broadcaster: 0
// Note: When the GAP role includes Peripheral and no v4.1 Controller features
//       are configured, MAX_NUM_BLE_CONNS must not be greater than 1
#ifndef MAX_NUM_BLE_CONNS
  #define MAX_NUM_BLE_CONNS             1
#endif

// bitmask of extended stack settings
#ifndef EXTENDED_STACK_SETTINGS
#define EXTENDED_STACK_SETTINGS         0x00
#endif

// bitmask which enables the offset of the overrides for BAW
#define CC2652RB_OVERRIDE_USED          0x02

// Maximum number of BLE HCI PDUs. If the maximum number connections (above)
// is set to 0 then this number should also be set to 0.
#ifndef MAX_NUM_PDU
  #define MAX_NUM_PDU                   5
#endif

// Maximum size in bytes of the BLE HCI PDU. Valid range: 27 to 255
// The maximum ATT_MTU is MAX_PDU_SIZE - 4.
#ifndef MAX_PDU_SIZE
  #define MAX_PDU_SIZE                  69
#endif
#endif //SYSCFG

// Maximum number of L2CAP Protocol/Service Multiplexers (PSM)
#ifndef L2CAP_NUM_PSM
  #define L2CAP_NUM_PSM                 3
#endif

// Maximum number of L2CAP Connection Oriented Channels
#ifndef L2CAP_NUM_CO_CHANNELS
  #define L2CAP_NUM_CO_CHANNELS         8
#endif

#ifndef MAX_NUM_WL_ENTRIES
#define MAX_NUM_WL_ENTRIES             16  // at 8 bytes per WL entry
#endif

#ifndef CFG_MAX_NUM_RL_ENTRIES
#ifdef GAP_BOND_MGR
#define CFG_MAX_NUM_RL_ENTRIES             GAP_BONDINGS_MAX // at 8 bytes per WL entry
#else
#define CFG_MAX_NUM_RL_ENTRIES             10  // at 8 bytes per WL entry
#endif
#endif

// Inactivity timeout in us
#ifndef RF_INACTIVITY_TIMEOUT
  #if defined(DEBUG_SW_TRACE) || defined(USE_FPGA)
    #define RF_INACTIVITY_TIMEOUT       BIOS_WAIT_FOREVER
  #else // !USE_FPGA
    #define RF_INACTIVITY_TIMEOUT       0
  #endif // DEBUG_SW_TRACE | USE_FPGA
#endif

// Powerup time in us
#ifndef RF_POWER_UP_DURATION
  #define RF_POWER_UP_DURATION          0
#endif

// Powerup duration margin in us
#ifndef RF_POWER_UP_DURATION_MARGIN1
  #ifdef CACHE_AS_RAM
    #define RF_POWER_UP_DURATION_MARGIN  550
  #else // !CACHE_AS_RAM
    #define RF_POWER_UP_DURATION_MARGIN  (314)
  #endif // CACHE_AS_RAM
#endif

// RF Driver Error Callback
#ifndef RF_ERR_CB
  #define RF_ERR_CB                      pRfErrCb
#endif

//
// Device Package and Evaluation Module (EM) Board
//
// The CC26xx device comes in three types of packages: 7x7, 5x5, 4x4.
// For each package, the user may change how the RF Front End (FE) is
// configured. The possible FE settings are provided as a set of defines.
// (The user can also set the FE bias, the settings of which are also provided
// as defines.) The user can change the value of RF_FE_MODE_AND_BIAS to
// configure the RF FE as desired. However, while setting the FE configuration
// determines how the device is configured at the package, it is the PCB the
// device is mounted on (the EM) that determines how those signals are routed.
// So while the FE is configurable, how signals are used is fixed by the EM.
// As can be seen, the value of RF_FE_MODE_AND_BIAS is organized by the EM
// board as defined by EMs produced by Texas Instruments Inc. How the device
// is mounted, routed, and configured for a user product would of course be
// user defined, and the value of RF_FE_MODE_AND_BIAS would have to be set
// accordingly; the user could even dispense with the conditional board
// compiles entirely. So too with the usage of the Tx Power tables. As can be
// seen in bleUserConfig.c, there are two tables, one for packages using a
// differential FE, and one for single-end. This too has been organized by TI
// defined EMs and would have to be set appropriately by the user.
//
// For example:
// Let's say you decided to build several boards using the CC26xx 4x4 package.
// For one board, you plan to use a differential RF FE, while on the other you
// wish to use a single ended RFN RF FE. You would then create your own Board.h
// (located by your preprocessor Include path name) that contains one of two
// defines that you create (say MY_CC26xx_4ID and MY_CC26xx_4XS). Then you can
// define your own choice of RF FE conditionally based on these defines
// (completely replacing those shown below), as follows:
//
//#if defined(MY_CC26xx_4ID)
//
//  #define RF_FE_MODE_AND_BIAS           (RF_FE_DIFFERENTIAL |               \
//                                          RF_FE_INT_BIAS)
//#elif defined(MY_CC26xx_4XS)
//
//  #define RF_FE_MODE_AND_BIAS           (RF_FE_SINGLE_ENDED_RFN |           \
//                                          RF_FE_EXT_BIAS)
//#else // unknown device package
// :
//
// In this way, you can define your own board I/O settings, and configure your
// RF FE based on your own board defines.
//
// For additional details and examples, please see the Software Developer's
// Guide.
//

// RF Front End Mode and Bias Configuration
#ifndef SYSCFG
#if defined(CC26XX)
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

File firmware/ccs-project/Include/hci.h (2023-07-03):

/******************************************************************************

 Group: WCS, BTS
 Target Device: cc13x2_26x2

 ******************************************************************************
 
 Copyright (c) 2009-2020, Texas Instruments Incorporated
 All rights reserved.

 IMPORTANT: Your use of this Software is limited to those specific rights
 granted under the terms of a software license agreement between the user
 who downloaded the software, his/her employer (which must be your employer)
 and Texas Instruments Incorporated (the "License"). You may not use this
 Software unless you agree to abide by the terms of the License. The License
 limits your use, and you acknowledge, that the Software may not be modified,
 copied or distributed unless embedded on a Texas Instruments microcontroller
 or used solely and exclusively in conjunction with a Texas Instruments radio
 frequency transceiver, which is integrated into your product. Other than for
 the foregoing purpose, you may not use, reproduce, copy, prepare derivative
 works of, modify, distribute, perform, display or sell this Software and/or
 its documentation for any purpose.

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
 Should you have any questions regarding your right to use this Software,
 contact Texas Instruments Incorporated at www.TI.com.

 ******************************************************************************
 
 
 *****************************************************************************/

/**
 *  @defgroup HCI HCI
 *  @brief This module implements the Host Controller Interface.
 *  For a detailed usage section describing how to send these commands and receive events,
 *  see the HCI Section of the User's Guide.
 *  @{
 */
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

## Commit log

2023-07-03 Added Altium source and output files for v1.0
    [Battery.SchDoc, Bill of Materials-OpenAXES.xlsx, OpenAXES.GBL, OpenAXES.GBO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]
2023-07-03 Added KiCad source files for v1.0
    [Adapter.kicad_sch, Battery.kicad_sch, OpenAXES.kicad_pcb, OpenAXES.kicad_sch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]
2023-07-04 Add 3D models for case, programmer and calibration fixture
    [D20-Calibrator.3mf, IMU-Case2_v12-Bottom.step, IMU-Case2_v12-Bottom.stl, IMU-Case2_v12-Top.step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]
2023-07-14 Add calibration scripts and documentation
    [log_imu9_2022-06-22_22-13-55.csv]
2023-07-20 Fixed link to source files in calibration README
2023-08-22 calibration: Improve documentation

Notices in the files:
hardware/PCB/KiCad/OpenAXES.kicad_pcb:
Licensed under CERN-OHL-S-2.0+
